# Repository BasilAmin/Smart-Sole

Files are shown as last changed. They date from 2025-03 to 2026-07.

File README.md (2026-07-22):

# Smart Sole

A lightweight, modular foot-sensing research prototype for real-time pressure monitoring, gait and behaviour classification, and anomaly detection.

[Project page](https://basilamin.com/projects/smart-sole/) ·
[Project book](./Smart%20Sole%20Project%20book.pdf) ·
[Presentation poster](./Smart%20Sole%20Presentation%20Poster.pdf) ·
[MIT License](./LICENSE)

## Overview

Smart Sole explores how embedded pressure sensors and machine learning could help identify unusual foot-pressure patterns associated with diabetic peripheral neuropathy.

The prototype places force-sensitive resistors at three areas of the foot:

- Heel
- Lateral arch
- Medial metatarsal

A Seeed Studio XIAO ESP32-S3 collects the sensor readings and transmits them over Bluetooth Low Energy. A Python application receives the data and experiments with a hybrid analysis pipeline combining neural-network behaviour classification with Isolation Forest anomaly detection.

> [!IMPORTANT]
> Smart Sole Version 1 is an experimental research prototype. It is not a certified medical device and must not be used for diagnosis, treatment, safety-critical monitoring, or as a substitute for professional medical care.

## Motivation

Diabetic peripheral neuropathy can reduce sensation in the feet, making potentially harmful pressure patterns more difficult to notice.

Smart Sole was inspired by my grandmother’s experience with the condition. The project investigates whether a wearable sensing system could act as a virtual feedback loop: observe pressure and movement, detect unusual patterns, and eventually provide useful feedback to the wearer.

## System Architecture

```text
┌──────────────────────────────┐
│ Force-Sensitive Resistors    │
│                              │
│  • Heel                      │
│  • Lateral arch              │
│  • Medial metatarsal         │
└──────────────┬───────────────┘
               │ Analogue readings
               ▼
┌──────────────────────────────┐
│ Seeed Studio XIAO ESP32-S3   │
│                              │
│  • Sensor sampling           │
│  • BLE GATT server           │
│  • Data formatting           │
└──────────────┬───────────────┘
               │ BLE notifications
               ▼
┌──────────────────────────────┐
│ Python Analysis Pipeline     │
│                              │
│  • Bleak BLE client          │
│  • Data preprocessing        │
│  • Behaviour classification │
│  • Anomaly detection         │
│  • Live visualisation        │
└──────────────────────────────┘
```

## Features

- Three-zone plantar-pressure sensing
- Wireless BLE data transmission
- Live sensor-data visualisation
- Experimental classification of standing, sitting, walking, limping, and pressure-avoidance behaviours
- Isolation Forest-based anomaly detection
- Pre-trained Keras models and sample datasets
- KiCad electronics files
- 3D-printable sole model
- PlatformIO-based firmware
- Project book and presentation poster

## Hardware

The Version 1 firmware is configured for the following components:

| Component | Purpose |
| --- | --- |
| Seeed Studio XIAO ESP32-S3 | Sensor acquisition and BLE communication |
| Heel FSR | Measures pressure near the heel |
| Lateral-arch FSR | Measures pressure near the outer arch |
| Medial-metatarsal FSR | Measures pressure near the forefoot |
| Custom sole and electronics | Holds and connects the system components |

### Firmware Pin Mapping

| Sensor | ESP32-S3 Pin |
| --- | --- |
| Heel | `A0` |
| Lateral arch | `A1` |
| Medial metatarsal | `A2` |

The current firmware transmits raw analogue readings. These values have not yet been converted into calibrated force or pressure units.

## BLE Data Format

The firmware publishes sensor readings as a UTF-8 string:

```text
HEEL <value>, LATERAL ARCH <value>, MEDIAL METATARSAL <value>, TIME <seconds>
```

Example:

```text
HEEL 1270, LATERAL ARCH 842, MEDIAL METATARSAL 2315, TIME 42
```

The firmware and Python clients use a custom BLE service and characteristic defined in the source code.

## Repository Structure

```text
Smart-Sole/
├── CAD/
│   ├── Schematic/                 # Electronics schematic files
│   ├── Smart_Sole/                # KiCad project files
│   ├── FSR LIB.kicad_sym          # FSR symbol library
│   └── SSFOOT.stl                 # 3D-printable sole model
│
├── Data management/
│   ├── Behaviour_regocnition_BLE.py
│   └── Smart_Sole_Models/         # Model-training experiments
│
├── Smart Sole Software/
│   ├── Behavioural detection model/
│   │   ├── Behaviour_model_training.py
│   │   └── *.keras                # Trained classification models
│   ├── Smart_Sole_Models/
│   │   ├── Smart_Sole_System_main.py
│   │   ├── Main.py
│   │   ├── Iso_forest_test.py
│   │   └── *.csv                  # Training and reference datasets
│   └── BLE_ScanForMAC             # BLE device discovery utility
│
├── SmartSole Firmware/
│   ├── src/main.cpp               # ESP32-S3 firmware
│   └── platformio.ini             # PlatformIO configuration
│
├── Smart Sole Presentation Poster.pdf
├── Smart Sole Project book.pdf
├── LICENSE
└── README.md
```

## Getting Started

### Prerequisites

For the firmware:

- Seeed Studio XIAO ESP32-S3
- Three force-sensitive resistors
- A computer with PlatformIO installed
- USB data cable

For the analysis software:

- Python 3
- Bluetooth Low Energy support
- A Python-compatible BLE adapter
- The dependencies listed below

### 1. Clone the Repository

```bash
git clone https://github.com/BasilAmin/Smart-Sole.git
cd Smart-Sole
```

### 2. Build and Upload the Firmware

Enter the firmware directory:

```bash
cd "SmartSole Firmware"
```

Build the project:

```bash
pio run
```

Upload it to the XIAO ESP32-S3:

```bash
pio run --target upload
```

Open the serial monitor:

```bash
pio device monitor --baud 9600
```

The device should begin advertising over BLE with the name:

```text
Smart Sole
```

### 3. Set Up the Python Environment

Return to the repository root and create a virtual environment:

```bash
python -m venv .venv
```

Activate it on macOS or Linux:

```bash
source .venv/bin/activate
```

Activate it on Windows:

```powershell
.venv\Scripts\activate
```

Install the packages used by the Version 1 scripts:

```bash
python -m pip install --upgrade pip
pip install bleak numpy pandas scikit-learn matplotlib tensorflow
```

### 4. Find the Smart Sole BLE Address

With the firmware running, use the BLE scanner:

```bash
python "Smart Sole Software/BLE_ScanForMAC"
```

Locate the device named `Smart Sole` and copy its address.

Replace the hard-coded BLE address in the Python script you intend to run. Depending on your operating system, the device identifier may appear as a MAC address or a platform-specific UUID.

### 5. Receive Raw Sensor Data

From the repository root, run:

```bash
python "Data management/Behaviour_regocnition_BLE.py"
```

This connects to the sole, subscribes to BLE notifications, and parses the three sensor readings.

### 6. Run the Behaviour Model

The main experimental behaviour-detection implementation is located at:

```text
Smart Sole Software/Smart_Sole_Models/Smart_Sole_System_main.py
```

Before running it, replace its machine-specific absolute paths with paths appropriate for your clone. When running from the repository root, the relevant files are:

```text
Smart Sole Software/Behavioural detection model/Behavioural_classification_model_R2.keras
Smart Sole Software/Smart_Sole_Models/Testing_R2_2.csv
```

Then run:

```bash
python "Smart Sole Software/Smart_Sole_Models/Smart_Sole_System_main.py"
```

## Analysis Pipeline

### Behaviour Classification

Sensor samples are collected into a fixed-length buffer, flattened, scaled, and passed to a TensorFlow/Keras classification model.

The Version 1 experiments include behaviour categories such as:

- Standing
- Sitting
- Walking
- Limping
- Stationary heel avoidance
- Dynamic heel avoidance
- Stationary lateral-arch avoidance
- Dynamic lateral-arch avoidance

### Anomaly Detection

The repository also experiments with scikit-learn’s `IsolationForest`.

Reference datasets represent expected readings for different behaviours. A new sample can then be compared with the relevant reference dataset to estimate whether it is anomalous.

This hybrid approach is intended to distinguish between:

1. The activity or behaviour being performed.
2. Whether the pressure pattern appears unusual for that behaviour.

## Version 1 Limitations

Smart Sole V1 is an early research implementation and currently has several limitations:

- Some Python scripts contain hard-coded BLE addresses.
- Some model paths are specific to the original development computer.
- The repository does not yet include a packaged command-line application.
- Python dependencies are not yet pinned in a `requirements.txt`.
- Sensor readings are raw ADC values rather than calibrated pressure measurements.
- The training data is limited and should not be treated as clinically representative.
- Model performance has not been clinically validated.
- Some folders contain earlier or duplicated experiments.
- Automated tests and continuous integration have not yet been added.

## Roadmap

Potential next steps include:

- [ ] Replace hard-coded paths and BLE addresses with a configuration file
- [ ] Add a reproducible `requirements.txt` or `pyproject.toml`
- [ ] Calibrate sensor readings into force or pressure units
- [ ] Add individual user-calibration workflows
- [ ] Expand and document the training dataset
- [ ] Add repeatable model-evaluation metrics
- [ ] Package the Python software into a single application
- [ ] Add automated firmware and software tests
- [ ] Improve the real-time visualisation interface
- [ ] Investigate wearable feedback methods
- [ ] Document hardware assembly and wiring
- [ ] Develop and evaluate a future Version 2 prototype
- [ ] Utilize LLMs for single model,time-series based highly descriptive feedback based off FSR data
- [ ] Increase the number of sensors

## Documentation

More information is available in:

- [Smart Sole project page](https://basilamin.com/projects/smart-sole/)
- [Smart Sole Project Book](./Smart%20Sole%20Project%20book.pdf)
- [Smart Sole Presentation Poster](./Smart%20Sole%20Presentation%20Poster.pdf)

## Contributing

Smart Sole is an experimental research project. Issues, technical suggestions, documentation improvements, and pull requests are welcome.

When contributing, please clearly distinguish between:

- Tested functionality
- Experimental functionality
- Proposed medical or clinical applications

Do not present experimental results as medical advice or clinically validated findings.

## License

This project is licensed under the [MIT License](./LICENSE).

## Author

Created by [Basil Amin](https://basilamin.com/).

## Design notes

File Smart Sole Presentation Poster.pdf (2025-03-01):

# ABSTRACT

# BACKGROUND

# MATERIALS, PARTS AND SOFTWARE

# HYPOTHESIS

Using AI to analyze foot pressure data can enable a system to provide feedback to Diabetics suffering from Diabetic Peripheral Neuropathy of anomalous foot movements, thereby reducing the risk of complications associated with this condition.

# SCIENTIFIC METHODOLOGY

# OUTCOMES

# DISCUSSION & CONCLUSION

# RECOMENDATION

# SIGNIFICANCE

# ACKNOWLEDGEMENTS

Peripheral Neuropathy refers to the set of neurological disorders concerning damage to the peripheral nervous system. Diabetic Peripheral Neuropathy (DPN) is the most common, affecting approximately 50% of Diabetics. Diabetics that suffer DPN suffer loss of sensation in the foot and are therefore susceptible to many different complications, such as:
- Ulcers 25% of DPN
- infected ulcers 55% of DPN with ulcers
- deformities 27% of DPN
- Amputations 20% with DPN
Being completely unaware of these complications because of the loss of sensation can result in incredibly severe consequences, including required amputation, and even death if the complication is left untreated.

Given humanity’s limited knowledge in the pathogenesis of this disorder, there is no existing cure, and the existing treatment is not impactful, being medication such as Opioids or Physical Therapy and orthotics which are primarily aimed to relieve the patient of a any pain caused by misfire by the nerves, addressing already established deformities and fixing gait patterns.

The Smart Sole project, using modern technology attempts to take a non-invasive, impactful approach to reducing the complications that are conceived by Diabetic Peripheral Neuropathy, by using artificial intelligence models to analyze foot pressure data, aiming to detect movements and habits that are likely to cause such complications to the user, and informing them in real time, as well as providing them with detailed feedback on their progression in text using a language model. Basically, the Smart Sole is simulating the biological way of informing a person that they are injured (pain) and trying to provide more detailed feedback on how they can progressively get better at avoiding these complications.

MATERIALS AND PARTS (per model):

ELECTRONICS:
- -XIAO ESP32-S3 MCU BOARD
- x2 LiPo Battery 3.7v, 400mAh
- X2 402 UX FSRs
- 408 UX FSR 100mm
- BLE Antenna
- X3 10KΩ resistors
- X2 LiPo Battery ports
- Jumper Wires
- 5V Linear Voltage Regulator
- Computer

OTHER PHYSICAL PARTS
- (generic) Insole
- 3D printed battery packs

SOFTWARE:
- PlatformIO development platform
- Llama 3.2 1B LLM
- MS Excel (data analysis)
- KiCAD

### PHASE 1: RECEIVING DATA

SMART SOLE FIRMWARE

### DEVICE RUNNING SMART SOLE SOFTWARE

### PHASE 2: PROCESS DATA AND DETECT BEHAVIOUR

PHASE 3: BEHAVIOUR BASED
ANOMALY DETECTION AND
PATEINT REAL TIME FEEDBACK

### PHASE 4: PERIODIC FEEDBACK, DATA ENCODING, INPUT AND OUTPUT (IN DEVELOPMENT)

### 1 second intervals

PARSE AND
PREPROCESS DATA

There are some future modifications I would like to introduce to make this project better in implementation, efficiency, and suited for mass production.

- I would like to improve the electronics system by creating a flex PCB rather than hand soldering and wiring the circuit. In addition, to specifically try and mitigate Charcot foot, I want to implement a temperature sensor, to examine the temperature of the foot.
- I want to increase the amount of training data and expand the behavioural analysis, such that users that pursue certain activities can have one suited to them, e.g. those who often play football so that when a user is playing on the field, they do not run in a way that may cause damage.
- A concept I would like to implement to make the whole process more efficient, is having a single LLM or SLM that is capable of taking in input data in a tokenized format and able to explain exactly what is happening, whether or not there is an anomaly, and explain each event in great detail
- At current, the process requires some form of connection or use of a PC CPU or GPU. With the rapid development of Small Language models, I would like to try and put the whole process into a single app, so that Wi-Fi connection is not required and the user does not suffer in the even that the mobile device breaks contact with the computer
- Implementation would be a substantial step to this project, and attempting to work with specialists and companies in this area would be a definite next step
- The Smart Sole project will contribute significantly to those who suffer from Diabetic Peripheral Neuropathy, as it is fundamentally replacing the role of nervous system in the area of their foot, and informing them virtually rather than informing them through the traditional method of pain.
- The Smart Sole is a novel idea, and as a project, it aims to help 50% of Diabetics who are destined to suffer from peripheral neuropathy and consequently foot deformities (+250,000,000 worldwide)
- Compared to the current treatment of Diabetic Peripheral Neuropathy, the Smart Sole would be a large stepping stone. The treatment that is used is mainly physiotherapy and some medication, however, there is still a substantial prevalence of the complications that come with Diabetic Peripheral Neuropathy mentioned in the Background. Because the Smart Sole specifically aims to mitigate these complications by trying to reduce habits or movements, in the long-term, the user will suffer less complications as they try to stop these habits.
- This project would also have widespread application, other than Diabetic Peripheral Neuropathy, this project can be applied to the elderly, in which this project can send an alert if they suffer a fall. This project can be applied to those who are in physiotherapy, and are relearning how to walk because of some traumatic accident. There are many existing applications for the Smart Sole.

This project would not have been possible without the help on certain people. I would like to thank my Father for his advice based on his medical expertise and telling me about PubMed, this was substantial for developing the formfactor of the hardware. I would like to thank my Support Teacher Jim McElroy, for his advice on the project development, helping me organize the data collection sessions with members of staff and students within the school, and for being my Support Teacher for this project. I would also like to thank Alexander Amini, for his substantial advice on the technical development aspects of the project, which contributed to its development. I would like to thank Dr. Ammar, a Diabetes specialist who gave advice on future implementation. I would like to thank Dr. Nuha Ibrahim, who gave me advice on the writing of the project book. I would like to thank my family, for their support and all those who offered and did take part in the data collection sessions. Thank you all very much.

Diabetic Peripheral Neuropathy (DPN) is a disorder with a prevalence level of 50% in people with Diabetes. This Neuropathological disorder can have substantial impacts on those who suffer from it, including ulcers, infected ulcers, foot deformities, Charcot foot, irregular gait pattern etc. These said complications contribute largely to substantial consequences suffered by those who suffer from DPN such as amputation, or in severe cases, death. The primary reason this is such a significant issue is because those who suffer from DPN lose all sensation in their feet, and therefore are completely unaware of the occurrence of such complications. Moreover, the present treatment for Diabetic Peripheral Neuropathy does not provide substantial aid, being mainly physical therapy, or prescribed medication, and there is no existing cure. The reasoning behind this is because our knowledge of the pathogenesis of DPN is relatively limited, and thus it is challenging to develop treatment without this knowledge.

The aim of this project, the Smart Sole, is to implement a never before seen, noninvasive method of attempting to prevent such complications by simply informing the user when an anomaly in foot pressure data is present, attempting to replace the role of the nervous system in the foot. The system utilizes hardware to collect data from the foot, and artificial intelligence to detect behavior and inform the user of anomalies in foot pressure data wirelessly on a device running the software. The Smart Sole also aims to provide periodic feedback, to try and mitigate risks in the long term as well, by creating a report utilizing generative ai.

MULTILAYER
PERCEPTRON NEURAL
NETWORK BEHAVIOUR
CLASSIFIER

### BEHAVIOUR LABEL OUTPUT

NO

### YES SELECT BEHAVIOUR LABEL SPECIFIC DATA

INJECT INPUT
DATASET WITH LABEL
SPECIFIC DATA

### ISOLATION FOREST

### YES

NO

ALERT USER VIA
DEVICE
NOTIFICATION ALERT

### TAKE NEW DATASET

### SAMPLED INPUT DATASET

### JSON

ENDCODER | LLAMA 3.2 1B
| LLM

### PRESET

QUESTIONS | INPUT QUESTIONS TO GUIDE TEXT OUTPUT

### DETAILED REPORT DISPLAYED IN APP REFERENCES

### INPUT DATA STRING: HEEL: x

LATERAL ARCH y,

### MEDIAL METATARSAL z, TIME

t,

### TRANSMITTED DATA STRING: HEEL: x

LATERAL ARCH y,

### MEDIAL METATARSAL z, TIME

t,

### IF INPUT BEHAVIOUR LABEL IS REGULAR

### IF INPUT DATA IS REGULAR RELATIVE TO THE BEHAVIOUR

### BEHAVIOUR LABEL OUTPUT

### AFTER SET TIME PERIOD

FIGURE 2
Figure 2 shows the electronics schematic, with all the mentioned components, as well as an image of an open Smart Sole model with the given schematic applied to the insole.

The primary objective of this project is to simply to give feedback to the user who suffers from Diabetic Peripheral Neuropathy when their foot is in such a position that can cause damage. The Smart Sole achieves this and successfully returns feedback to the user by:
- Detecting anomalies specific to behaviour
- Capable of alerting the user when an anomaly is present or progressing.
- Detecting Behaviour
The periodic progression tracking and detailed feedback by LLM is still in progress. This system successfully achieves it’s initial aim. The system was carefully validated and tested to ensure its purpose is fulfilled.

In addition, the behaviour detection model is trained over many collected samples, from many distinct subjects to account for factors such as total mass, weight distribution throughout the foot, etc.

Ongoing development includes more training of behavioural detection model and implementation of LLM to output detailed and tracked feedback.

Figure 3 is a flowchart that demonstrates the system architecture, by taking in data, transmitting it to a device running the software wirelessly, parsing the data, detecting the behaviour using a Multilayer perceptron model then detecting whether or not an anomaly is present using the Isolation Forest anomaly detection algorithm.

### FIGURE 3

### 1. CREATE METHOD FOR DATA COLLECTION

### 2. COLLECT DATA FOR MODEL TRAINING AND BEHAVIOUR COMPARISON

### 3. COMPARE AND PLOT BEHAVIOUR DATA TO ANALYZE HOW DIFFERENT BEHAVIOURS DIFFER IN DATA

### DATA COLLECTION

DESIGN,

### CREATE AND TEST SYSTEM

### CREATE TESTING MODELS

### PROGRAM FIRMWARE TO TRANSMIT INPUT DATA STRING THROUGH BLE

### RECEIVE AND READ RAW INPUT DATA

PARSE AND PREPROCESS DATA
TO SUITABLE INPUT FORMAT (4 INPUT FEATURES)

X, X1

, X2,

....XT
Y, Y1

, Y2

, ....YT
Z, Z1

, Z2,

....ZT
1, 2, 3 .........T

### HOST DATA COLLECTION SESSIONS

PARTICIPANTS CARRY OUT DYNAMIC AND STATIONARY LABELS FOR MLP BEHAVIORAL DETECTION MODEL

### CREATE PARENT CSV FILE AND SUB-FILES STORING EACH BEHAVIOUR

### PLOT AND ANALYZE PATTERNS IN BEHAVIOUR SPECIFIC PRESSURE DATA

### COMPARE DIFFERENCES

### MODIFY LABELS BASED ON DIFFICULTY OF DIFFERENTIATION

DESIGN AND TEST HARDWARE

CREATE AND TRAIN BEHAVIOUR DETECTION MODEL

As a result, this system provides feedback to the user on foot-pressure anomalies that are based on their behaviour to aim to prevent future complications that may occur as a result of Diabetic Peripheral Neuropathy

CREATE AND TRAIN ANOMALY
DETECTION MACHINE LEARNING ALGORITHM

CREATE SYSTEM GUI TO EXAMINE OUTPUTS

### DESIGN SCHEMATIC AND BREADBOARD PROTOTYPE

### CREATE MOBILE PROTOYPE PROGRAM TRANSMISSION FIRMWARE AND TEST BLE

### EXAMINE PRACTICALITY

(comfortability, functionality,

### is it implementable etc.)

### EXAMINE AND VERIFY TRANSMITTED SENSOR OUTPUT

CREATE
SEQUENTIAL MLP
TENSORFLOW
MODEL

### TRAIN FROM COLLECTED DATA

### TEST MODEL FROM TEST DATASET

### LOAD AND TEST FOR MODEL VALIDATION

### CREATE BEHAVIOUR BASED DATASET SELECTOR

### CREATE BEHAVIOUR SPECIFIC DATSETS WITH REGULAR BEHAVIOUR

### IMPORT AND FIT ISOLATION FOREST MODEL WITH SEPARATE DATASETS FOR VALIDATION

### EXAMINE AND COMPARE EXPECTED OUTPUTS WITH ACTUAL OUTPUTS

### MODIFY DATSETS IF NEEDED

### WRITE PROGRAM TO TAKE INPUTS

### SHOW AND PLOT PRESSURE POINTS LIVE

### DISPLAY BEHAVIOUR

### DISPLAY BOOLEAN VALUE FOR ANOMALY DETECTION

(02, n.d.; An Often Preventable Complication of Diabetes-Diabetic Neuropathy - Symptoms & Causes, n.d.; Marmolejo et al., 2018; Gandhi et al., 2022; Armstrong et al., 2023; Margolis et al., 2002; Alam et al., 2017; Barrell & Smith, 2019; Hicks & Selvin, 2019; Etiology, Epidemiology, and Disparities in the Burden of Diabetic
Foot Ulcers | Diabetes Care | American Diabetes Association, n.d.; How Quickly Does Diabetic Neuropathy
Progress?, n.d.; Lawler et al., 2023; Perveen et al., 2024; Gordois et al., 2003) (Diabetic Foot & Vascular (https://www.zotero.org/google-docs/?8UeYIY) Guidance – GP Gateway, n.d. (FIGURE 1)) (https://www.zotero.org/google-docs/?sjfXff)

# The Smart Sole: Using Hybrid AI Analysis to Inform Patients On Foot Pressure Anomalies For Peripheral Neuropathy

BASIL AMIN
THE SMART SOLE

2025

FIGURE 1
Figure 1 shows
3 images of
the said
complications,
including
ulcers,
deformities
and calluses

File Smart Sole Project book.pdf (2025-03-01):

# THE SMART SOLE: USING HYBRID AI ANALYSIS TO INFORM PATIENTS ON FOOT PRESSURE ANOMALIES FOR PERIPHERAL NEUROPATHY

### CREATED BY BASIL AMIN

# ABSTRACT:

Diabetic Peripheral Neuropathy (DPN) is a disorder with a prevalence level of 50% in people with Diabetes. This Neuropathological disorder can have substantial impacts on those who suffer from it, including: ulcers, infected ulcers, foot deformities, charcot foot, irregular gait pattern etc. These said complications contribute largely to substantial consequences suffered by those who suffer from DPN such as amputation, or in severe cases, death. The primary reason this is such a significant issue is because those who suffer from DPN lose all sensation in their feet, and therefore are completely unaware of the occurrence of such complications. Moreover, the present treatment for Diabetic Peripheral Neuropathy does not provide substantial aid, being mainly physical therapy, or prescribed medication, and there is no existing cure. The reasoning behind this is because our knowledge of the pathogenesis of DPN is relatively

limited, and thus it is challenging to develop treatment without this knowledge.

The aim of this project, the Smart Sole, is to implement a never before seen,

noninvasive method of attempting to prevent such complications by simply informing the user when an anomaly in foot pressure data is present, attempting to replace the role of the nervous system in the foot. The system utilizes hardware to collect data from the foot, and artificial intelligence to detect behaviour and inform the user of anomalies in foot pressure data wirelessly on a device running the software. The Smart Sole also aims to provide periodic feedback, to try and mitigate risks in the long term as well, by creating a report

utilizing generative ai.

## 1.2 Current solutions, medical treatment and diagnosis.. 7

# 1: INTRODUCTORY

### 1.1 Diabetic Peripheral Neuropathy

Peripheral Neuropathy refers to the set of neurological disorders that concern damage to the Peripheral Nervous System, which is a significant neurological network that sends and receives signals from the central nervous system (the brain, and the spinal cord) to all other parts of the body. The most common and impactful sort being Diabetic Peripheral Neuropathy (chronic), affecting roughly 50% (approx. 250 million Diabetics) (Alam U., et al., 2017) of patients who suffer from Diabetes, as well as being associated with a poor prognosis, and a high mortality rate. Its occurrence is dependent on a multitude of factors such as: age, duration of Diabetes, glucose control and type 1 or type 2 diabetes.

Diabetic Peripheral Neuropathy typically occurs in the legs or feet, most commonly the feet. It is caused by high blood sugar which inflicts damage upon the nerves; consequently, the patient loses all sensation in their feet or legs and remains uninformed on any injury or health related occurrences in the feet, as they cannot feel pain, and experience loss or abnormal feeling of temperature (Pineda-Gutierrez, et al., 2017). Examples of damage that a patient may be unaware of includes ulcers, and deformities, which can possibly result in much required amputation.

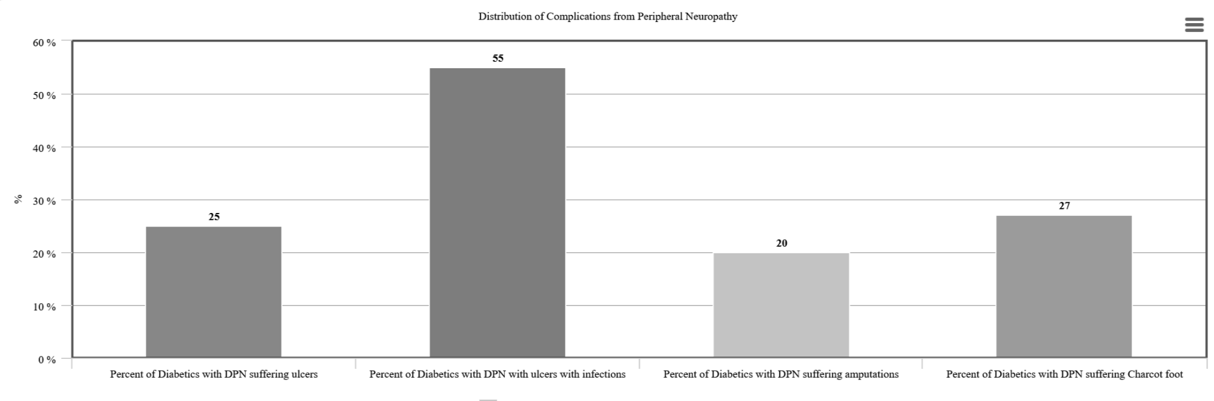
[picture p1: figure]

Figure: 1.A

Figure 1.A thoroughly demonstrates the distribution of complications that are typical for patients who suffer DPN (Diabetic Peripheral Neuropathy). This data, originating from published studies (Chapter
8) demonstrates the significant portions that these complications take of Diabetics with DPN. Diabetics with Diabetic Peripheral Neuropathy suffering from: Ulcers, infected ulcers, amputations and charcot foot (disfigurement). These complications all contribute to the mortality rate of patients diagnosed with Diabetic Peripheral Neuropathy, with a 2023 study (ref. 13) demonstrating that 1 in 5 of patients diagnosed with DPN, pass away due to these complications.

This can usually be drawn back to the fact that patients suffering from Diabetic Peripheral Neuropathy lose sensation within their feet, which can be a significant contributor to the mortality rate, amputation rate, feet deformities such as Charcot foot and delayed diagnosis due to unawareness of early complications such as ulcers.

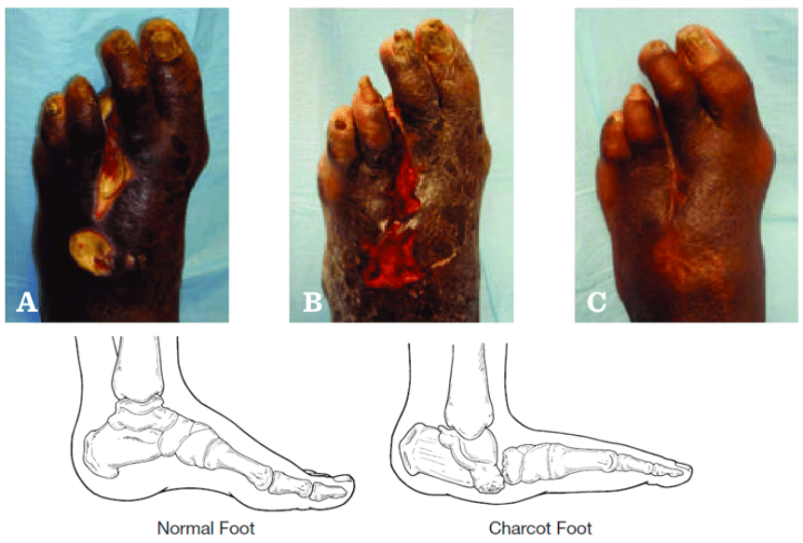
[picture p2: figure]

Figure 1.B

Figure 1.B (Charcot Foot — Jason Morris, DPM, n.d.; FIGURE 3 Progression of a Diabetic Foot Ulcer from Necrotic Wound Base..., n.d.)) (https://www.zotero.org/google-docs/?7NLFNH) Shows the development of a Diabetic foot ulcer and Charcot foot.

### 1.2 Current solutions, medical treatment and diagnosis

The current solutions to the consequences of Peripheral Neuropathy exist with the prime goal of reducing the progression of Diabetic Peripheral Neuropathy, reducing any inflicted nerve pain that may be a consequence of nerve damage and to manage its complications and restore function. Due to the relatively substandard knowledge of the pathogenesis of Diabetic Peripheral Neuropathy that we have, its treatment is oriented around relieving its symptoms rather than curing. There is currently no existing cure or drug on the market for Diabetic Peripheral Neuropathy treatment, proposing a significant problem to a significant number of people. Examples of current treatment include: Antidepressants (to depolarize neurotransmitters) , Opioids such as Oxycodon (as a front-line therapeutic agent) and Physical Therapy methods such as acupuncture. These forms of relief are primarily based on our current pathogenesis of Diabetic Peripheral Neuropathy, which is that it may interact with neurological and blood supply disorders, and is caused by insulin deficiency, insulin resistance, hyperglycemia and dyslipidemia. In addition, Orthotics attempts to aid the feet, however, it is quite strange to try to alleviate a problem after it has been caused, specifically when you know it will occur.

At current, there are 2 distinct processes to diagnosis: the conventional method, being referenced in type 2 diabetes screening, whereas in Traditional Chinese Medicine diagnosis is reliant on previous medical records of the patient, accompanied by detailed physical examination records, specifically neural examination records; the diagnosis is fully based on symptoms from clinical examination. If an anomalistic manifestation has been observed, the patient is typically recommended to see a neurophysiologist.

It is understandable that these methods are in use, given our lack of knowledge in the pathogenesis of Diabetic Peripheral Neuropathy; however given our current technological era, as companies, research organisations and academic institutions continue to develop marvels of cyber-human engineering, such as state of the art controllable prosthetics, Neuralink brain chips, etc. It should be evident that a technological solution is the answer to accommodate a problem as simple as providing feedback to a Diabetic suffering Diabetic Peripheral Neuropathy, who is suffering significantly reduced sensation?

### 1.3 The Smart Sole

The Smart Sole is a never-before seen method aiming to virtually inform Diabetics who suffer from Diabetic Peripheral Neuropathy, since they suffer loss of sensation in their feet, preventing the previously said complications from occurring. It uses a structured method to do this, utilizing physical hardware to collect data, wireless transmission using BLE (Bluetooth Low Energy) and various data processing, machine learning algorithms and artificial intelligence models to provide detailed scheduled feedback and real time feedback to the user.

PROJECT HYPOTHESIS: Using AI to analyse foot pressure data can enable a system to provide feedback to Diabetics suffering from Diabetic Peripheral Neuropathy of anomalous foot movements, thereby reducing the risk of complications associated with this condition.

# 2: SCIENTIFIC METHODOLOGY

### 2.1 Objectives

The three primary aims of this project are:

- To Alert the user in real time of foot-pressure anomalies that may cause harm, such as wounds.
- To distinguish between what is normal and what is abnormal, first I will program a behaviour classification model to detect user activity to define what exactly is “regular” data and “irregular” data.
- To be capable of differentiating between normal and abnormal, I will then program another model to detect whether or not the given data is normal or abnormal
- Finally, if the input is abnormal, an alert is sent. Otherwise, the next data input is examined.
- Provide detailed interpretable feedback to users, periodically, so that they are able to improve upon the feedback given to them, and track their progression.
- Take many samples of data over a given time period
- Store these data samples

- Feed the samples from the current and last period as well as input questions to a language model
- Receive and display a natural language output to the user

### 2.2 Materials and software

ELECTRONICS:
--XIAO ESP32-S3 MCU BOARD
-x2 LiPo Battery 3.7v, 400mAh -X2 402 UX FSRs
-408 UX FSR 100mm
-BLE Antenna
-X3 10KΩ resistors
-X2 LiPo Battery ports
-Jumper Wires
-5V Linear Voltage Regulator -Computer

OTHER PHYSICAL PARTS
-(generic) Insole
-3D printed battery packs

SOFTWARE:
- PlatformIO development platform -Llama 3.2 1B LLM
-MS Excel (data analysis)
-KiCAD

### 2.3 Methodology

First and foremost, before developing any software or programs, data is required to
- Identify the key factors and relationships in data features that allow distinction of behaviour
- Train models
- Create an accurate expectation to hold capability to identify if there is an error e.g. hardware problem

To collect data, I initially modelled a prototype electronics system in KiCAD and then a breadboard (Figure 2.A). This was done to identify any errors that may occur early on in the hardware before wiring and soldering together parts and potentially wasting them. The aim of this prototype was to simply transmit sensor data (force sensitive resistors) through Bluetooth or BLE (Bluetooth Low

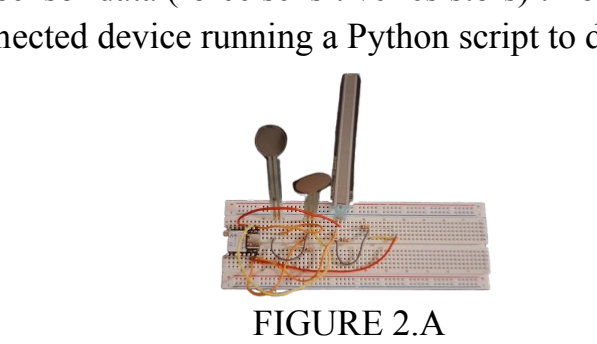
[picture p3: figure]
FIGURE 2.A

energy) to a connected device running a Python script to display all the received data.

Figure 2.A is the initial breadboard prototype made to detect errors. It features the same components found in the final model, (Electronics, section 2.3) and uses wiring through connected terminals to send power and signals.

The reasoning behind placing the force sensitive resistors in this configuration, is because the main pressure points when a foot makes contact with a surface is in these locations (Figure 2.B)

After validating and testing the hardware, I built, wired and soldered a number of insole models that are capable of transmitting data wirelessly. Then I organized data collection sessions for students and staff in my school as well as members of my family. In each session, each participant would wear the insole, complete a dynamic or stationary activity, and their data would be collected. The regular activities included:
- Walking
- Standing
- Sitting

Additionally, anomalous activities based on common irregular gait patterns and foot pressure positions that are commonly present in those who suffer from Diabetic Peripheral Neuropathy were also completed and included:
- Limping
- Heel avoidance (stationary)
- Heel avoidance (dynamic)
- Lateral Arch pressure (stationary)
- Lateral Arch pressure (dynamic)
Dynamic meaning that this irregularity takes place while the patient is walking and stationary meaning this irregularity takes place when the patient is standing still or sitting.

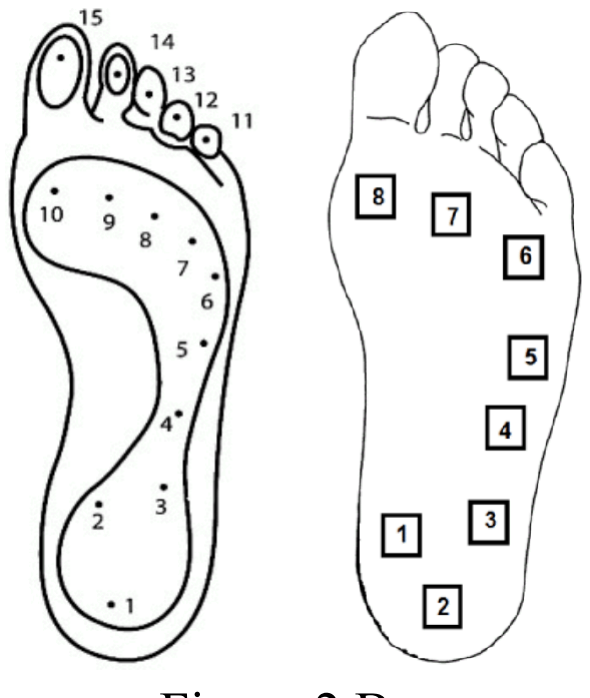
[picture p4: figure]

Figure 2.B
Figure 2.B (Pineda-Gutierrez et al. 2019) conveys the main pressure points when the foot makes contact with a flat surface. The points (1, 2, 3) surround the heel, points (4, 5 , 6, 7) are on the Lateral Arch and points (10, 9) are on the Medial Metatarsal.

When this data was collected, in its raw format, was simply hundreds of lines of input strings, where each line contains the 3 labelled input features and their current data values in the form of 12-bit ADC (Analog to digital converter). I then plotted some session behaviours to compare the differences and similarities in each behavioiur’s data (example Figure 2.C).

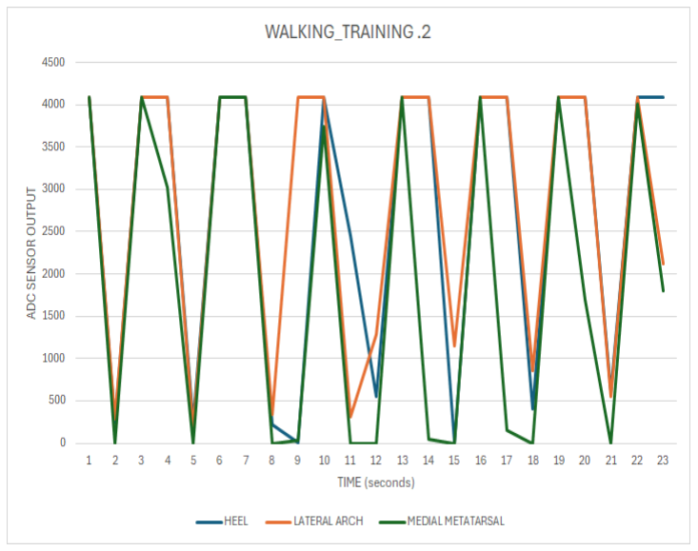
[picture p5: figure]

Figure 2.C

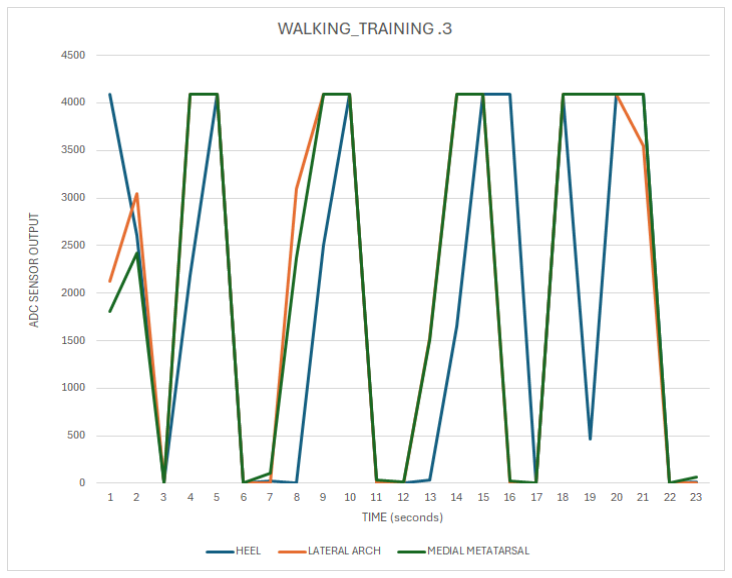
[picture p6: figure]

Figure 2.C shows 2 examples of the plotted data in the form of trend graphs, where the y axis represents the current ADC value and the x axis represents time in seconds. The current activity being executed in both of these sessions are walking, being a regular behaviour. The swing is apparent when the values spike down and the stomp is seen when the value spikes up. The rest of this data is found in the project Github repository linked at the end of this paper.

Then, I worked on trying to refine the formfactor of the hardware (figure 2.D) by cleaning up the wiring, and creating a quick and easy way to plug in the power supply. Similar to the data collection session models, this one worked well, however was more directed to refining user aspects. The schematic for this model (figure 2.D)was also made to test any modifications if necessary.

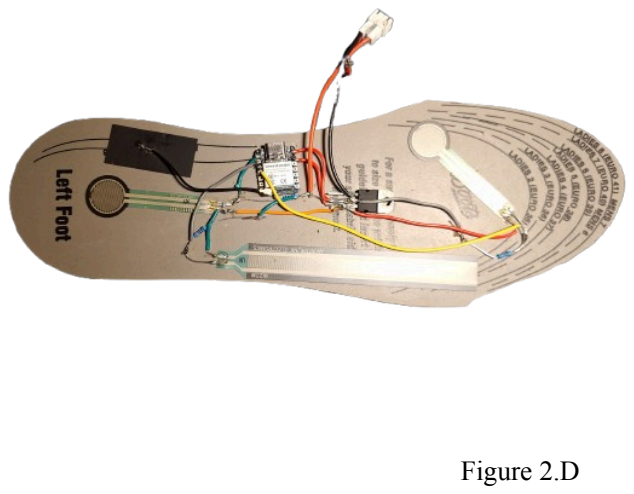
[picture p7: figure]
Figure 2.D
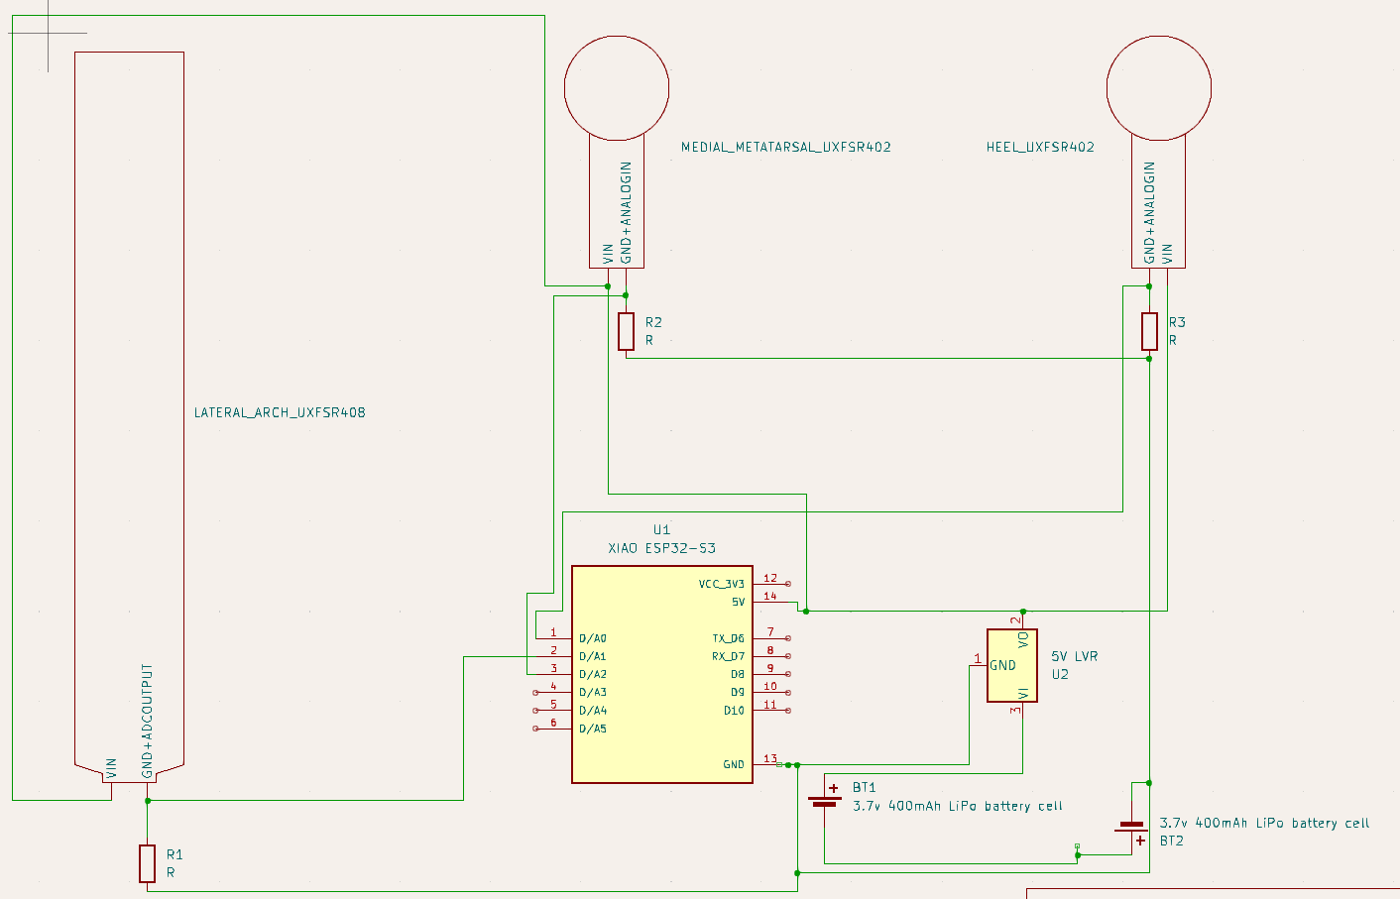
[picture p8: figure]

Figure 2.D shows the hardware on the bottom of the Smare Sole model. The side with the electronics is inserted downwards facing the sole. The 3 FSRs are sensing foot pressure data and the XIAO ESP32-S3 is receiving and transmitting it. The FSRs are in a 10KΩ resistor voltage divider circuit configuration. A Bluetooth antenna and a Lithium Polymer battery port are connected to the MCU.
Then, I began developing computer programs in an iterative manner, with the aim of detecting the user’s behaviour from foot pressure data, detecting if there is an irregularity in this data or selected behaviour and then alerting the user.

I started by creating a piece of computer software that is capable of receiving a stream of data via Bluetooth and then displaying it on a computer terminal where each line is a string of the data from each of the 3 pressure points, receiving this data at a rate of 1 line per second. Then, to find irregularity in the data, the system must first identify what the current behaviour of the user is.

To do this, I developed a Deep feedforward neural network behaviour detection model also known as a multilayer perceptron to take in an input matrix containing each of the pressure points in the form: Where x is the Heel input value, y is the Lateral Arch input value and z is the Medial Metatarsal input value. The input string also contains the time T in seconds, however, is not necessary for the neural network output.

I wrote a data parser to take the input string and then preprocess the data to this format for the behaviour detection model.

The Behavioural detection model is made up of 4 layers in total, with 2 hidden layers consisting of 128 neurons (Figure 2.E)

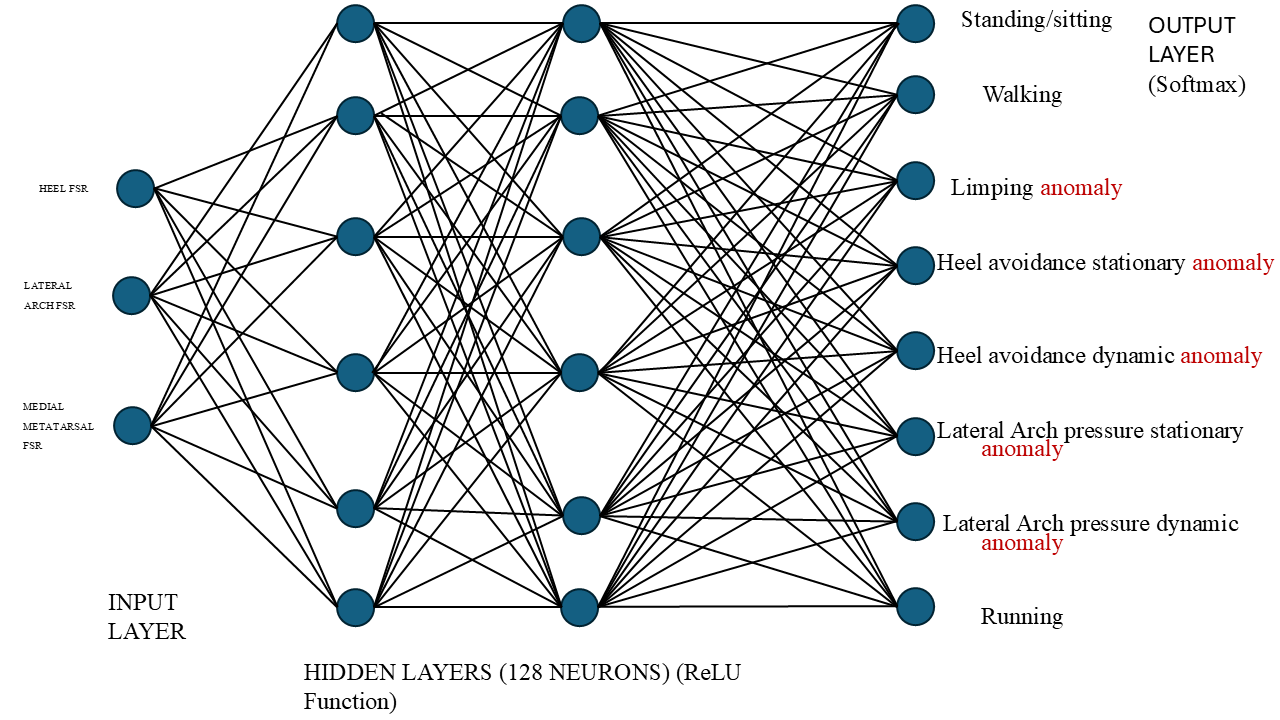
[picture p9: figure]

Figure 2.E
Figure 2.E shows the structure of the Multilayer perceptron, with 3 input features in the Input layer, 128 neurons in the hidden layers, and 8 labels in the output layers. These labels have been selected since these are the most common behaviours in people with DPN in gait patterns, etc.

This model then must be trained in order to output accurate labels in accordance to the input data. I then created csv files of each session and behaviour, and then trained the model on each of these datasets as well as my own datasets that I myself have collected, to allow it to accurately output predictions for the behaviour. There are some preset anomalous labels for common irregular movements and positions that those who suffer DPN do.

Then, to specifically detect anomalies, I applied a machine learning algorithm known as Isolation Forest that specifically aims to detect irregular values in datasets. To accurately find all anomalies, the behaviour is given to a function that aims to select a dataset from a group of datasets that contain regular data relative to the behaviour. If an anomalistic behaviour was selected, this step is skipped.

The selected regular dataset is then appended to the input dataset given from the sensors. This was added to the software to try and standardize the values in the dataset so that the Isolation Forest Algorithm can accurately distinguish between anomalies and regular values. I sampled these regular datasets from training data from the behavioural detection model. Then, I tested the system in a run once configuration. When applied however, this should run continuously until the connection via Bluetooth has disconnected, meaning the device was turned off. I decided to test each system individually before using them all together to make error detection easier.

I then tested the accuracy of the model by creating a testing dataset, and another test dataset to examine the accuracy of the Isolation Forest Model.

Then, I programmed a GUI to display the system metrics. This consisted of a graph displaying the current value of each sensor Input, a string output displaying the current behaviour, then a boolean statement as to whether or not the behaviour or data is anomalous.

THE FOLLOWING SECTION OF THE METHODOLOGY IS STILL IN PROGRESS AT THE TIME OF THE WRITING OF THIS PAPER.
PROPOSED METHOD:

Then, for tracking the user’s progress, providing them with detailed feedback, and ultimately allowing them to improve in the long term, I will start by taking the Llama 3.2 1B parameter model. I will start by making a suitable input format that can be given to the Language model. This format will be JSON (JavaScript Object Notation). This input should consist of sampled anomalous data collected throughout the week. A csv file will store these files, from being extracted after processing in the real time feedback process. Then, I will write paired sample outputs, one from the current period, and one from the previous period. They will be tagged so that the Language model can differ between time periods.

Then, I will put this data and tokenize it then pass it through the model for training. It will then be trained and capable of providing periodic feedback.

# 3: RESULTS

The highly beneficial results of this project include:

- An accurate behaviour detection neural network model
- A system capable of informing the user when an anomaly is present
- An attempt at preventing future potential complications
- A system overall that can provide behaviour based feedback based on pressure in the user’s feet.

The results of this project start from the hardware.

The initial result is that there is an electronics system that returns and transmits pressure data wirelessly from the main pressure points in the foot, using firmware programmed to transmit FSR data via BLE

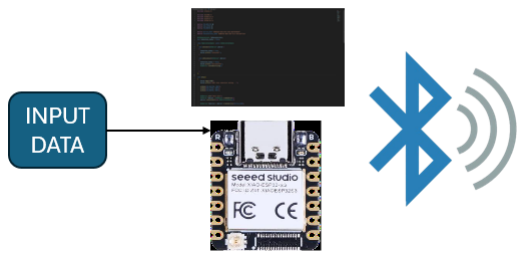
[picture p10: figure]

Figure 3.A
Figure 3.A shows the transmission of BLE, where the input sensor data goes through an MCU running firmware.

It is capable of sending a string in the following format:
bytearray(b'HEEL 0, LATERAL ARCH 0, MEDIAL METATARSAL 0, TIME 0')

When this is picked up, the data is first preprocessed before given to the model. It is parsed into the
format: [[1238 4095 995 4095 4095 3691 4095 4095 3885 0 3981 | 0 | 0
2735
0 | 8 4095 | 81 4095 4095 4095 4095 4095 4095 4095 4095 2092 | 0
3519 | 0]]
This is a 1D array, converted from the original matrix format, by flattening it before input.

Then, the Behaviour detection model received this data, and upon initial testing, gave poor results, with accuracy of 25% and a loss of 3.0760. This is not suitable for implementation, and thus, I created a greater dataset for training and testing, where I created a greater distribution of data among all behaviours, shuffled them into patterns to allow the model to recognize transition between behaviours, and modified the model architecture, adding 5 layers, 1 being hidden, the rest being for data normalization, dropout and flattening. The extra hidden layer is 32 neurons, and should overall be better for the task.

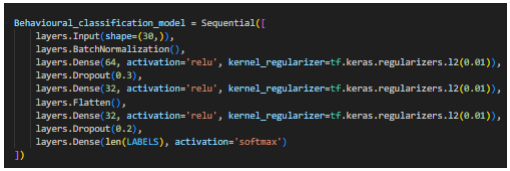
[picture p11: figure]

The total volume of the data consisted of 14,400 data points, with 600 lines with 3 features creating 1,800 data points per behaviour. These were all collected in sessions of 10 minutes per behaviour with the Smart Sole collecting data. Additionally, sitting and standing were separated movements and running was removed. The format of the data was:
4095,4095,3824,4095,4095,3772,4095,4095,3565,4095,4095,3607,4095,4095,3573,409 5,4095,3552,4095,4095,3641,4095,4095,3930,4095,4095,3389,4095,4095,3273,6
(Example taken from: Heel avoidance dynamic)
The last value is the referral to the label.

Then, in order to expand the dataset, increase variability, I wrote a computer program to sample the training and test data in random batches, that made sense in real world application (Example: Walking for 2 minutes, stop and stand for 30 seconds, limp for 2 minutes etc.) and did this by creating
maximum and minimum batch sizes. This led to a relatively substantial increase, leading to an accuracy level of roughly 76.3% after cross examination with multiple datasets that derive from the same file samples as the training data .

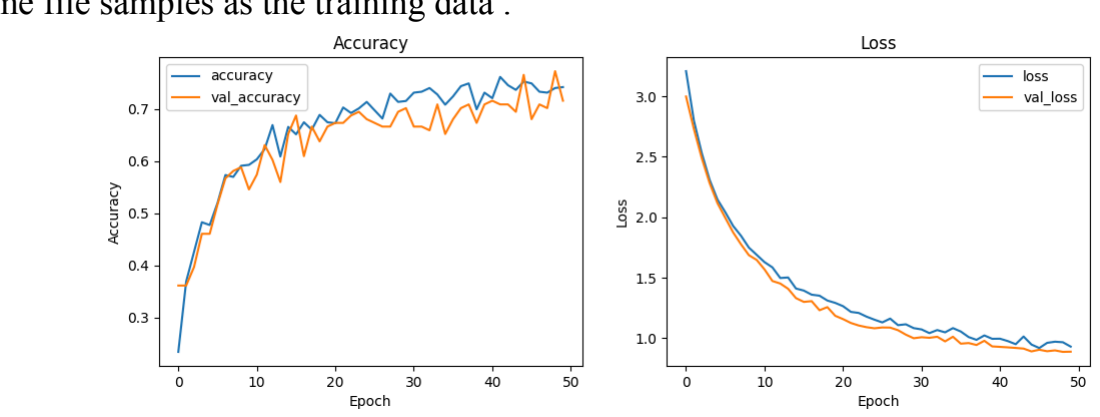
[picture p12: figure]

Figure 3.B
Figure 3.B demonstrates the development in accuracy of the improved training method, and the decrease in loss value as the number of Epochs (maximum capacity 50) increases. This was then repeated with an extended testing and training set, with over 50,000 data points. The testing data had roughly 27,000 data points. The model accuracy then increased to approximately 87% after cross testing.

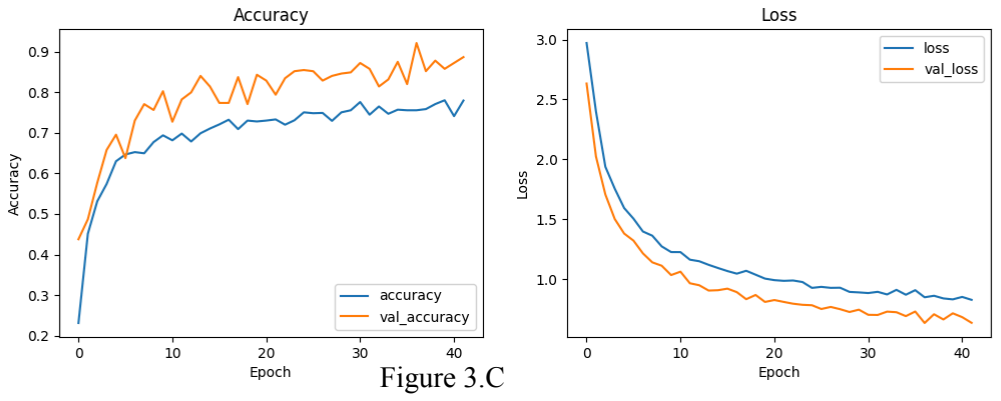
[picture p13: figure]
Figure 3.C

Figure 3.C shows the accuracy of the model, per epoch increased. The second graph to the right hand side demonstrates the loss value per epoch.

After increasing the Behavioural Detection models training data to nearly 100,000 data points and the testing data to 83,000 data points, where each data point is 1 feature per input dataset, by utilizing random batch sampling for both the testing and training data, the model shows an accuracy of 93.4% accuracy, even levelling with industry and medical level wearable Behaviour detection technology, of roughly 93.8% (Weizman et al., 2023). (https://www.zotero.org/google-docs/?SxaDXP)

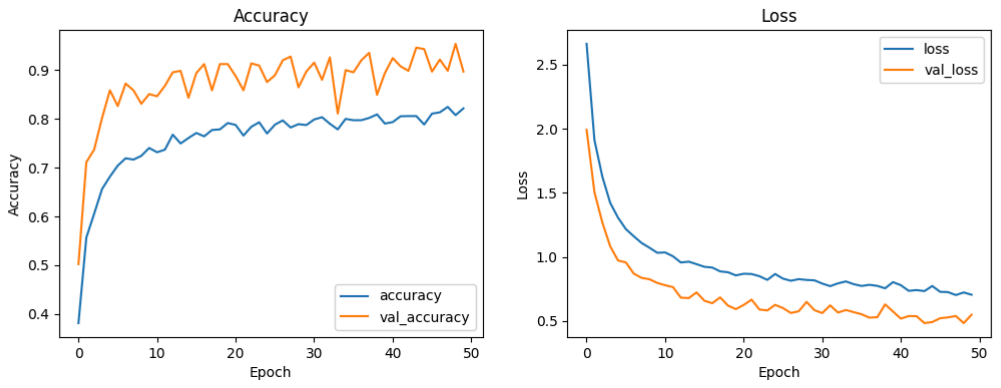
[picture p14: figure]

Figure 3.D
Figure 3.4 shows the highest accuracy measurement from the Smart Sole Behavioural detection model to date, showing accuracy levels of 93.4%. The graph on the left showing accuracy per epoch and the graph on the right showing loss value per epoch. As a result, using a deep feedforward neural network to detect Behaviour from foot pressure data, can be accurate in accordance to the industry standard.

Additionally, the Smart Sole’s anomaly detection system, that examines the input data and appends it with data regular for the current behaviour, is successfully capable of taking the MLP’s output, and selecting a sample dataset to append the input with. Upon initial testing, I found that the dataset was too small, thus I applied the same method I did to the MLP, and sampled data from my Training set, to behaviour specific files.

Then, I tested the model a number of times, with different data from different datasets. For instance, (Figure 3.E) I tested the limping data with walking data, to see if the machine learning algorithm can accurately detect the input dataset (limping) in the regular dataset (walking) and it was able to accurately determine this data was anomalous. This was tested again among other sets (Figure 3.F) to examine validity. Due to the large size of the dataset, the model was accurately able to detect the anomalous dataset.

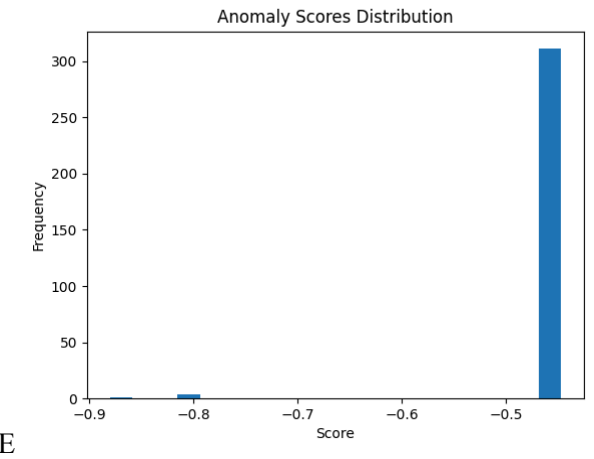
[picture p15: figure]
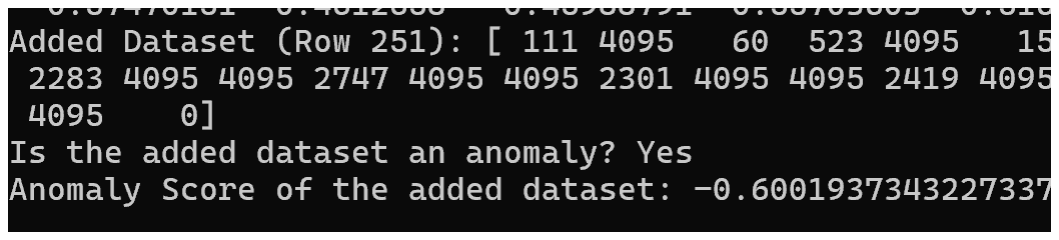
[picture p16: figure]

FIGURE 3.E
Figure 3.E shows the validation output of the computer program to examine the metrics of the algorithmic output, as well as a graph produced to show the anomaly scores distribution. In this special case, the regular data is standing and the input data is limping, thus leading to a huge skew in the anomaly scores distribution. The contamination value for the model at this time was 0.0316.

FIGURE 3.F

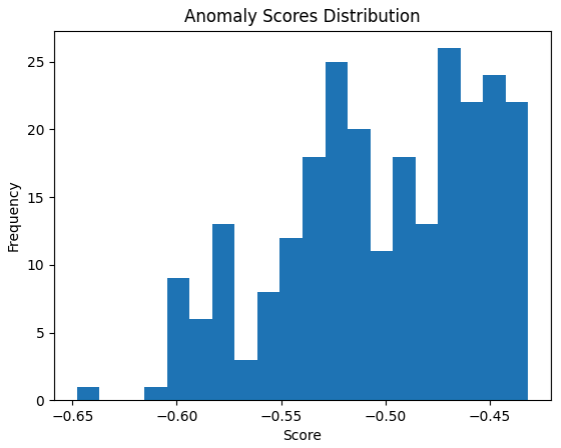
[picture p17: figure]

Figure 3.F shows the validation output of the computer program to examine the metrics of the algorithmic output, as well as a graph produced to show the anomaly scores distribution. The special case here is that this input set, in theory, should be more difficult to detect as an anomaly, because the walking data is constantly changing with the swing and stop, and there may be a near alignment with some of the regular values and the anomalous input value. However, it was still successfully detected.

Similarly, I wanted to see if I had given a regular dataset its own “regular” data, would it still detect it as an output?

After testing this, I found that they were not detected as anomalies. And thus the model is accurate enough to detect that a dataset is not regular compared to regular datasets to that behaviour.

As a result, a system with the capability of detecting behaviour, and providing feedback based on this detected behaviour to aid those who suffer from DPN by informing them on foot pressure anomalies to try and reduce complications in creating and functioning.

# 4: CONCLUSION AND DISCUSSION

### 4.1 Comparison to criteria

The original criteria for this project was:
- To Alert the user in real time of foot-pressure anomalies that may cause harm, such as wounds.
- To distinguish between what is normal and what is abnormal, first I will program a behaviour classification model to detect user activity to define what exactly is “regular” data and “irregular” data.
- To be capable of differentiating between normal and abnormal, I will then program another model to detect whether or not the given data is normal or abnormal
- Finally, if the input is abnormal, an alert is sent. Otherwise, the next data input is examined.

When compared to the original criteria, the initial, and most important point in the criteria has been fulfilled. The second part is still in development. The system is able to classify behaviour, define what is abnormal and normal and return feedback to the user. The method that is used to do this is relatively accurate, and after individually testing the systems and gathering results, it is fair to determine that this method proves the initial project hypothesis.

# 5: IMPACT AND IMPORTANCE

### 5.1 Diabetic Peripheral Neuropathy increase

As more and more people begin to suffer from Diabetes, with an expected 783 million to have Diabetes by 2045 according to the International Diabetes Federation, there will be a substantial increase in the population of those who have Diabetic Peripheral Neuropathy, given it’s prevalence level of 50%.

This means more and more people will suffer from Diabetic Peripheral Neuropathy complications, and consequently face severe consequences, such as amputation. The Smart Sole is a method to try and stop these complications before they happen. The current treatment of Orthotics, medication and physical therapy, aims to try and aid these complications after they occur, which is an unorthodox approach to such a problem. However, this is understandable because our understanding of the disorder is limited.

### 5.2 Widespread significance

Additionally, this will allow patients to know when they are getting anomalies, in real time, serving as a “virtual nervous system”, by alerting them. The Smart Sole (once added) will also be able to help with long term feedback to try and mitigate complications in the long term.

It is also important to note that fundamentally, this is a system that detects behaviour and examines if data is regular for a given behaviour. This has widespread application! This can be applied to the elderly to detect and alert for falls, those who suffer from mental disorders, etc.

# 6: RELATED WORK

Kim, M.-J., Han, J.-H., Shin, W.-C., & Hong, Y.-S. (2024). Gait Pattern Identification Using

Gait Features. Electronics, 13(10), Article 10. https://doi.org/10.3390/electronics13101956

Manna, S. K., Hannan Bin Azhar, M. A., & Greace, A. (2023). Optimal locations and

computational frameworks of FSR and IMU sensors for measuring gait

abnormalities. Heliyon, 9(4), e15210. https://doi.org/10.1016/j.heliyon.2023.e15210

Shaikh, M. F., Salcic, Z., & Wang, K. (2015). Analysis and selection of the Force

Sensitive Resistors for gait characterisation. 2015 6th International Conference on

Automation, Robotics and Applications (ICARA), 370–375.

https://doi.org/10.1109/ICARA.2015.7081176

Weizman, Y., Tan, A. M., & Fuss, F. K. (2023). The Use of Wearable Devices to Measure

Sedentary Behavior during COVID-19: Systematic Review and Future

Recommendations. Sensors (Basel, Switzerland), 23(23), 9449.

https://doi.org/10.3390/s23239449

Yu, L., Zheng, J., Wang, Y., Song, Z., & Zhan, E. (2015). Adaptive method for real-time

gait phase detection based on ground contact forces. Gait & Posture, 41(1),

269–275. https://doi.org/10.1016/j.gaitpost.2014.10.019

# 7: APPENDICES

PROJECT GITHUB REPOSITORY:

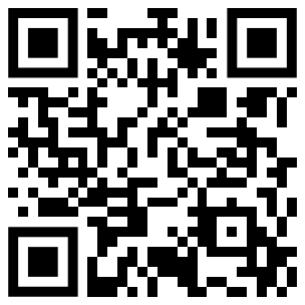
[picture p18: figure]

DATA COLLECTION FORM:

SMART SOLE TRIAL. DATA COLLECTION TERMS AND CONDITIONS.
FULL NAME :
DATA COLLECTION PROCESS AND DATA PROCESSING
The data collection process for the Smart Sole project, spanning over a week, will consist of 3 participants a day, taking part in movement activities, while wearing an insole which collects their foot pressure data. This data will then be transmitted to the participants mobile device via BLE (Bluetooth Low Energy) through a Bluetooth Terminal (created by Innovator’s Den) while simultaneously being screen-recorded, for each specific activity. The hardware in the insole has been flashed with firmware specifically to connect to both Android and Apple devices. These activities will take place over lunch, where participants will meet Basil Amin in “Insert location”. You will each be assigned a day, in which you will partake in the data collection process. After the data collection process is complete for that day, each participant will share the screen recording file (.MP4, .MP3, etc.) with Basil Amin, and this will be your data collection process finished.
Your contribution of data will be purposed to train artificial intelligence models, which will improve their ability to detect common foot-pressure anomalies through behavioural recognition, and provide progressive feedback on potentially damaging habits, and preventative measures to complications that occur commonly with Diabetic Peripheral Neuropathy . This will allow Diabetics who suffer from Diabetic Peripheral Neuropathy, an opportunity to potentially increase their lifespan and lessen the risks of complications (ulcers, infected ulcers, deformities, amputation etc.) by keeping them aware virtually, since they are unable to feel pain in their feet.
TERMS AND CONDITIONS:
- I Shall not disclose any information that I have learned about the Smart Sole project from participating in the data collection process to any organisation, public bodies, or people.
- I Fully agree to partake in the data collection process, and follow all instructions, given above in this form.
- I agree to delete all recordings of data collection after they have been sent, and confirmed to be interpretable (not corrupted, correct filetype etc.) and to not send any data from the Smart Sole data collection process to any organisation, public bodies or people.
- I understand that there is a risk or possibility for problems to occur with LiPo batteries catching fire if they are damaged during the session or prior session and that Basil Amin is not liable for such an occurrence.
- By signing this form, I agree to all Terms and Conditions, and am happy to proceed with the data collection process.
NAME |
SIGNATURE |
DATE |

# 8: CITATIONS

02: Overview of diabetic foot problems (NHS England) – Diabetes Foot Screening.

(n.d.). Retrieved January 1, 2025, from

https://www.diabetesframe.org/nhs-england/02-overview-of-diabetic-foot-problems-

nhs-england-2/ (https://www.diabetesframe.org/nhs-england/02-overview-of-diabetic-foot-problems-nhs-england-2/)

Alam, U., Riley, D. R., Jugdey, R. S., Azmi, S., Rajbhandari, S., D’Août, K., & Malik, R.

A. (2017). Diabetic Neuropathy and Gait: A Review. Diabetes Therapy, 8(6),

1253–1264. https://doi.org/10.1007/s13300-017-0295-y

An often preventable complication of diabetes-Diabetic neuropathy—Symptoms &

causes. (n.d.). Mayo Clinic. Retrieved January 1, 2025, from

https://www.mayoclinic.org/diseases-conditions/diabetic-neuropathy/symptoms-cau

ses/syc-20371580 (https://www.mayoclinic.org/diseases-conditions/diabetic-neuropathy/symptoms-causes/syc-20371580)

Armstrong, D. G., Tan, T.-W., Boulton, A. J. M., & Bus, S. A. (2023). Diabetic Foot

Ulcers: A Review. JAMA, 330(1), 62–75. https://doi.org/10.1001/jama.2023.10578

Barrell, K., & Smith, A. G. (2019). Peripheral Neuropathy. The Medical Clinics of North

America, 103(2), 383–397. https://doi.org/10.1016/j.mcna.2018.10.006

Charcot Foot—Jason Morris, DPM. (n.d.). Retrieved January 5, 2025, from

https://www.northcountyfootankle.com/charcot-foot/

Diabetic Foot & Vascular Guidance – GP Gateway. (n.d.). Retrieved January 1, 2025,

from

https://www.coventryrugbygpgateway.nhs.uk/pages/diabetic-foot-vascular-guidance

/ (https://www.coventryrugbygpgateway.nhs.uk/pages/diabetic-foot-vascular-guidance/)

Etiology, Epidemiology, and Disparities in the Burden of Diabetic Foot Ulcers | Diabetes
Care | American Diabetes Association. (n.d.). Retrieved January 1, 2025, from

https://diabetesjournals.org/care/article/46/1/209/148198/Etiology-Epidemiology-an

d-Disparities-in-the (https://diabetesjournals.org/care/article/46/1/209/148198/Etiology-Epidemiology-and-Disparities-in-the)

Facts & figures. (n.d.). International Diabetes Federation. Retrieved January 5, 2025,

from https://idf.org/about-diabetes/diabetes-facts-figures/

FIGURE 1.B Progression of a diabetic foot ulcer from necrotic wound base... (n.d.).

ResearchGate. Retrieved January 5, 2025, from

https://www.researchgate.net/figure/Progression-of-a-diabetic-foot-ulcer-from-necro

tic-wound-base-A-to-surgical_fig2_328948516 (https://www.researchgate.net/figure/Progression-of-a-diabetic-foot-ulcer-from-necrotic-wound-base-A-to-surgical_fig2_328948516)

Gandhi, M., Fargo, E., Prasad-Reddy, L., Mahoney, K. M., & Isaacs, D. (2022).

Diabetes: How to manage diabetic peripheral neuropathy. Drugs in Context, 11,

2021-10–12. https://doi.org/10.7573/dic.2021-10-2

Gordois, A., Scuffham, P., Shearer, A., Oglesby, A., & Tobian, J. A. (2003). The Health

Care Costs of Diabetic Peripheral Neuropathy in the U.S. Diabetes Care, 26(6),

1790–1795. https://doi.org/10.2337/diacare.26.6.1790

Hicks, C. W., & Selvin, E. (2019). Epidemiology of Peripheral Neuropathy and Lower

Extremity Disease in Diabetes. Current Diabetes Reports, 19(10), 86.

https://doi.org/10.1007/s11892-019-1212-8

How Quickly Does Diabetic Neuropathy Progress? (n.d.). Retrieved January 1, 2025,

from

https://www.healthline.com/health/diabetic-neuropathy-progression#life-expectancy

Lawler, F. H., Mold, J. W., Liao, X., & Bard, D. E. (2023). Peripheral Neuropathy in Older

People Is Associated with Reduced Life Expectancy. The Journal of the American

Board of Family Medicine, 36(3), 431–438.

https://doi.org/10.3122/jabfm.2022.220306R1

Margolis, D. J., Allen-Taylor, L., Hoffstad, O., & Berlin, J. A. (2002). Diabetic Neuropathic

Foot Ulcers: The association of wound size, wound duration, and wound grade on

healing. Diabetes Care, 25(10), 1835–1839.

https://doi.org/10.2337/diacare.25.10.1835

Marmolejo, V. S., Arnold, J. F., Ponticello, M., & Andersen, C. A. (2018). Charcot Foot:

Clinical Clues, Diagnostic Strategies, and Treatment Principles. American Family

Physician, 97(9), 594–599.

Perveen, W., Ahsan, H., Rameen Shahzad, Fayyaz, S., Zaif, A., Paracha, M. A.,

Nuhmani, S., Khan, M., & Alghadir, A. H. (2024). Prevalence of peripheral

neuropathy, amputation, and quality of life in patients with diabetes mellitus.

Scientific Reports, 14(1), 14430. https://doi.org/10.1038/s41598-024-65495-2

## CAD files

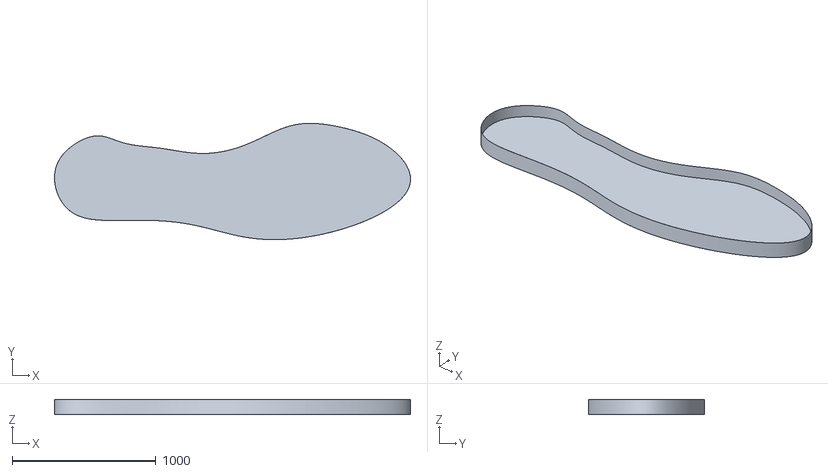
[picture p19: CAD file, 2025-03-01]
CAD/SSFOOT.stl
2474.1 x 808.4 x 102.8

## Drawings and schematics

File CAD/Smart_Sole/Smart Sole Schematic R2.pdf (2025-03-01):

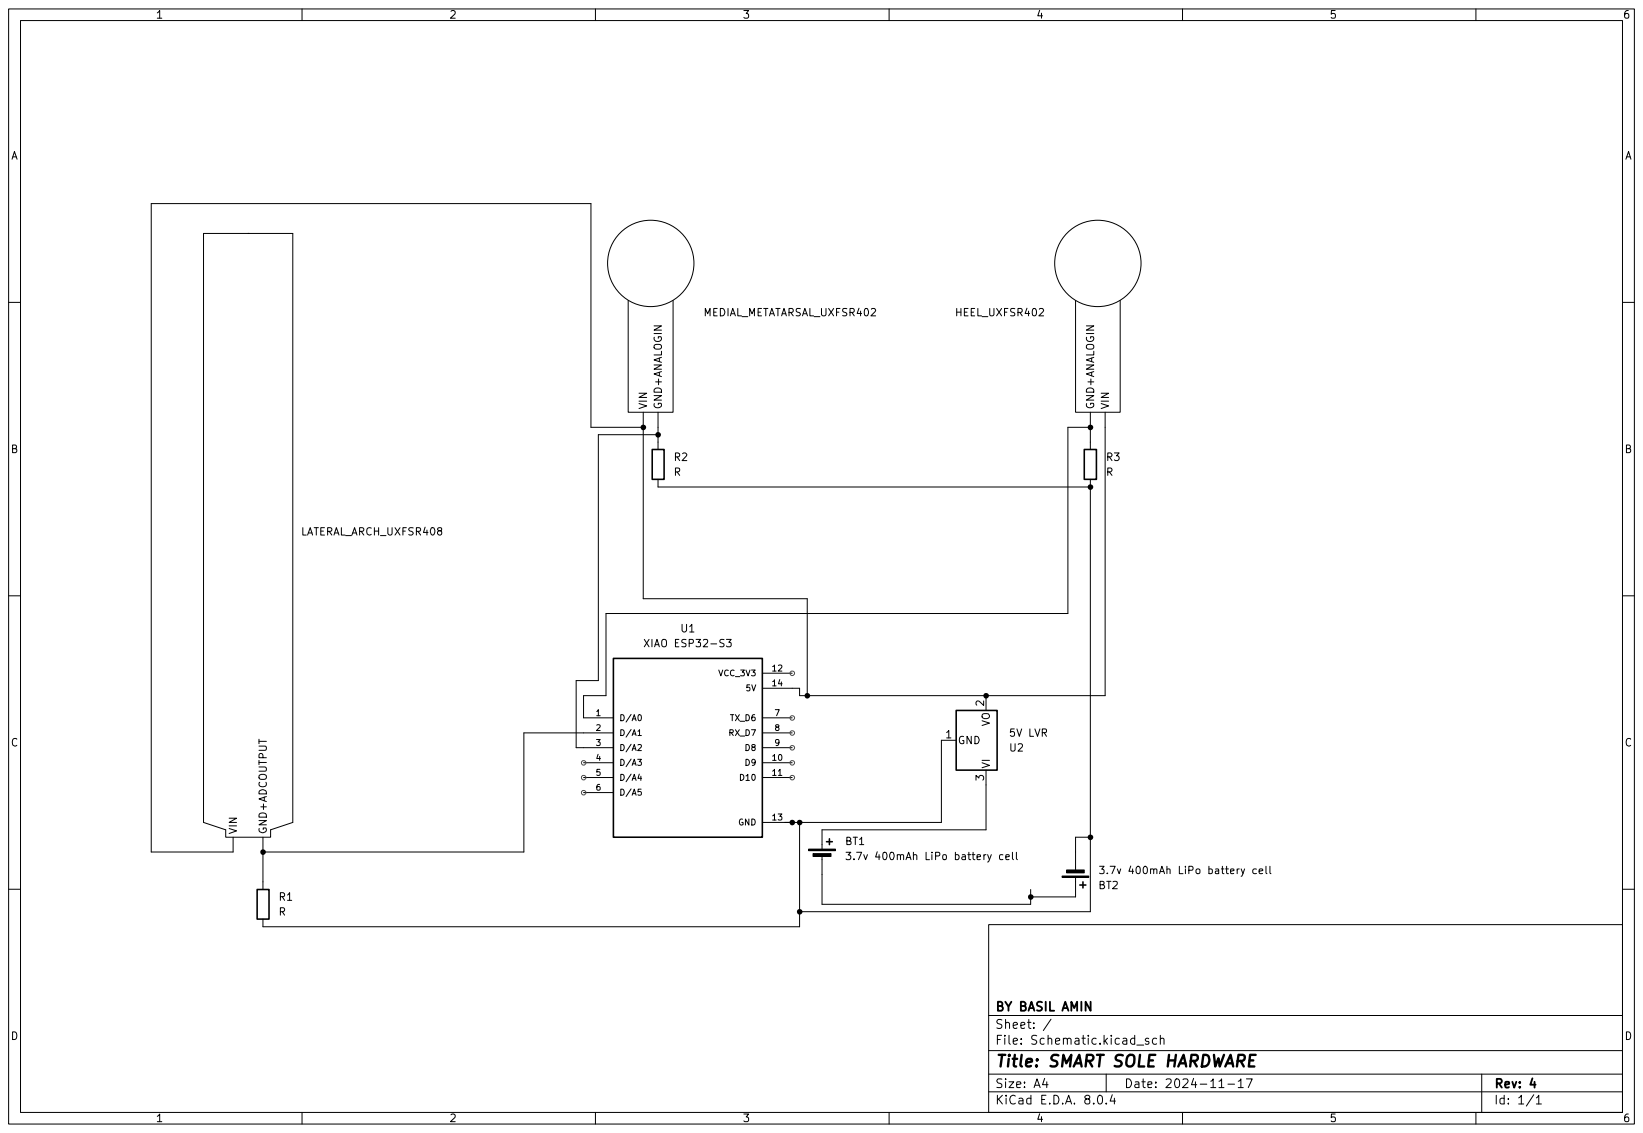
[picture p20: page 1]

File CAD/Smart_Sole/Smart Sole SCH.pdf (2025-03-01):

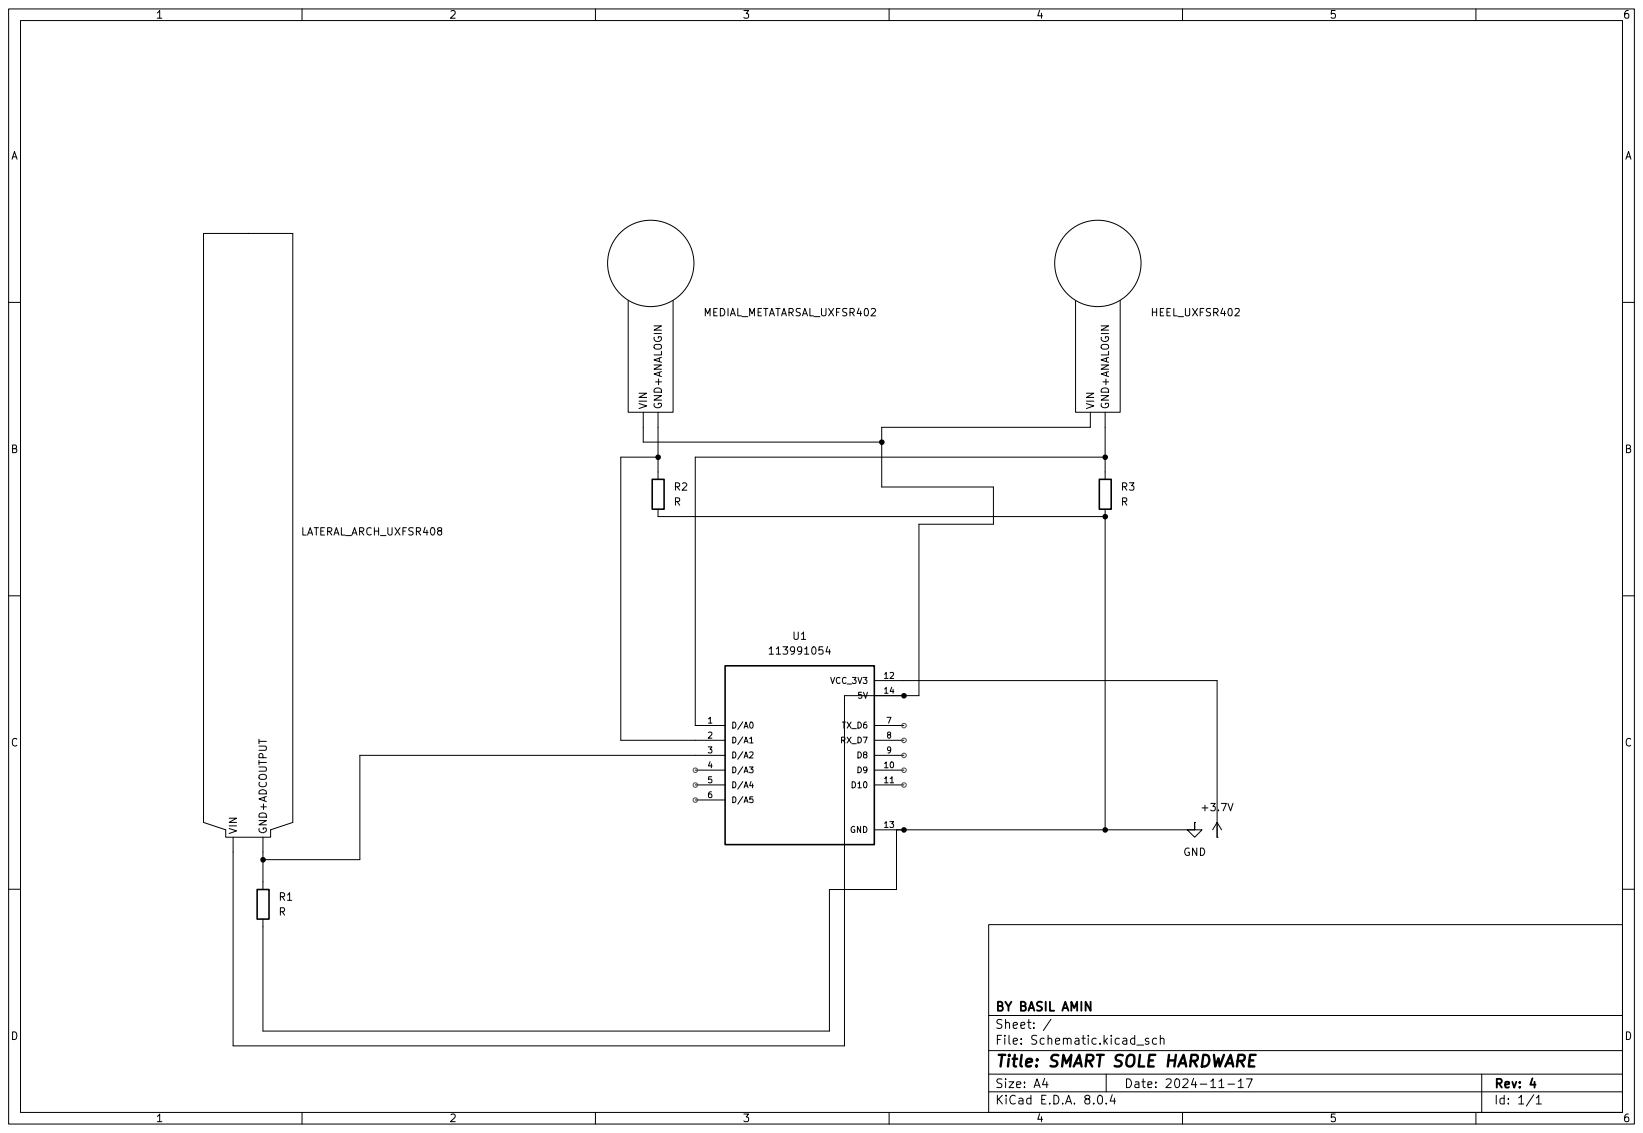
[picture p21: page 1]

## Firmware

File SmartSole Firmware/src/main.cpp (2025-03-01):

#include <Arduino.h>

#include <BLE2902.h>
#include <BLEDevice.h>
#include <BLEUtils.h>
#include <BLEServer.h>

#define FSR_HEELPIN A0
#define FSR_LATPIN A1
#define FSR_MEDPIN A2

#define Service_UUID "d90562d9-6939-4431-b382-48e783366d67"
#define Characteristic_UUID "0a002f5b-d64e-4667-9cc3-c0c5c857715a"

BLECharacteristic *pCharacteristic;
bool Connection_status = false;

class MyServerCallbacks: public BLEServerCallbacks
{
  void onConnect(BLEServer* pServer )
  {
    Connection_status = true;
    Serial.println("Connected!");
  }

  void onDisconnect(BLEServer* pServer)
  {
    Connection_status = false;
    Serial.println("Disconnected");
    BLEDevice::startAdvertising();
    

  }  
};
 

void setup()
{
    Serial.begin(9600);
    Serial.println("Smart Sole connection testing ...");

    pinMode(FSR_HEELPIN, INPUT);
    pinMode(FSR_LATPIN, INPUT);
    pinMode(FSR_MEDPIN, INPUT);


    BLEDevice::init("Smart Sole");
    BLEServer *pServer = BLEDevice::createServer();
    pServer->setCallbacks(new MyServerCallbacks());

    BLEService *pService = pServer->createService(Service_UUID);

    pCharacteristic = pService->createCharacteristic(
    Characteristic_UUID, 
    BLECharacteristic::PROPERTY_NOTIFY |
     BLECharacteristic::PROPERTY_READ);
    

    pCharacteristic->addDescriptor(new BLE2902());


    pService->start();

    BLEAdvertising *pAdvertising = BLEDevice::getAdvertising();
    pAdvertising->addServiceUUID(Service_UUID);
    pAdvertising->setScanResponse(true);
    pAdvertising->setMinPreferred(0x06);
    pAdvertising->setMinPreferred(0x12);
    BLEDevice::startAdvertising();
    
    Serial.println("Started advertising connectivity");



}

void loop()
{
    if (Connection_status){
    int heel_val = analogRead(FSR_HEELPIN);
    int lat_val = analogRead(FSR_LATPIN);
    int med_val = analogRead(FSR_MEDPIN);

  int  time = millis() / 1000;

    String InputData_stream =
            "HEEL " + String(heel_val) +
        ", LATERAL ARCH " + String(lat_val) +
        ", MEDIAL METATARSAL " + String(med_val) + ", TIME " + String(time);
  

    pCharacteristic->setValue(InputData_stream.c_str());
    pCharacteristic->notify();

    Serial.println("Data: " + InputData_stream);




delay(1000);
    }
}
